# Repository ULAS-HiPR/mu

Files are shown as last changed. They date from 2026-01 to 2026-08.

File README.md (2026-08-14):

# Mu

Mu is a standalone SiPM/scintillator cosmic-ray detector and flight logger developed alongside the [Ogma avionics stack](https://sean-osullivan.com/projects/ogma/). It is designed to fly as its own black box: battery power in, particle and pressure data logged to onboard flash, then post-flight readout.

> [!CAUTION]
> **Rev 1 assembly corrections:** The `MICROFC-60035-SMT-TR1` SiPM footprint nets are reversed. On an existing Rev 1 PCB, mount U3 180 degrees from the orientation indicated by the footprint's pin-1 marker. This puts SiPM pin 3 (cathode) on PCB pad 1, the filtered HV-bias node, and SiPM pin 1 (anode) on PCB pad 3, the U5 inverting-input node. Pins 2 (fast output) and 4 (no connect) then exchange two unused PCB pads.
>
> The Rev 1 footprint also connects centre pad 5 to AGND. [Onsemi specifies pin 5 as no connect and recommends leaving the paddle unsoldered and floating](https://www.onsemi.com/download/data-sheet/pdf/microc-series-d.pdf). On the working board, a tiny piece of Blu Tack on the PCB beneath pad 5 kept the centre paddle off the board, and the sensor was attached to four small solder balls around the outer pads. A new PCB revision should correct the pin 1/pin 3 net mapping and leave pad 5 floating instead of relying on either assembly workaround.

## Hardware

- 50 x 50 x 20 mm BC-408 plastic scintillator.
- Onsemi MicroFC-60035 6 x 6 mm SiPM biased at about 30 V.
- OPA656/OPA814-class transimpedance readout around a 2.5 V reference.
- STM32F042 controller, W25Q128 external flash, and MS5607 barometer.
- Optional CAN interface; standalone logging does not depend on the Ogma stack.

## Repository

- `mu.kicad_sch`, `power.kicad_sch`, and `mu.kicad_pcb` - KiCad hardware design.
- `fabrication/` - Rev 1 manufacturing outputs.
- `Lib/` - project symbols, footprints, and 3D models.
- `SiPM Test Samples/` - raw oscilloscope samples.

Firmware, the field dashboard, and current flight preparation are on [`mu/f042-bringup`](https://github.com/ULAS-HiPR/mu/tree/mu/f042-bringup).

## Status

Mu has detected and logged real particle pulses on the bench and flew at Mach26, but it did not record a clean in-flight particle run. The reproduced fault is mechanical over-compression of the scintillator/SiPM stack. Packaging and flight validation remain in progress; Mu is not yet flight-proven.

## Manufacturing support

Rev 1 PCB fabrication was sponsored through [EasyEDA Education](https://easyeda.com/education) and manufactured by [JLCPCB](https://jlcpcb.com/). The board was designed in KiCad and imported into EasyEDA Pro for the sponsorship and manufacturing workflow.

## More information

See the [Mu project write-up](https://sean-osullivan.com/projects/mu/) for the detector, bring-up failures, pulse captures, and flight diagnosis.

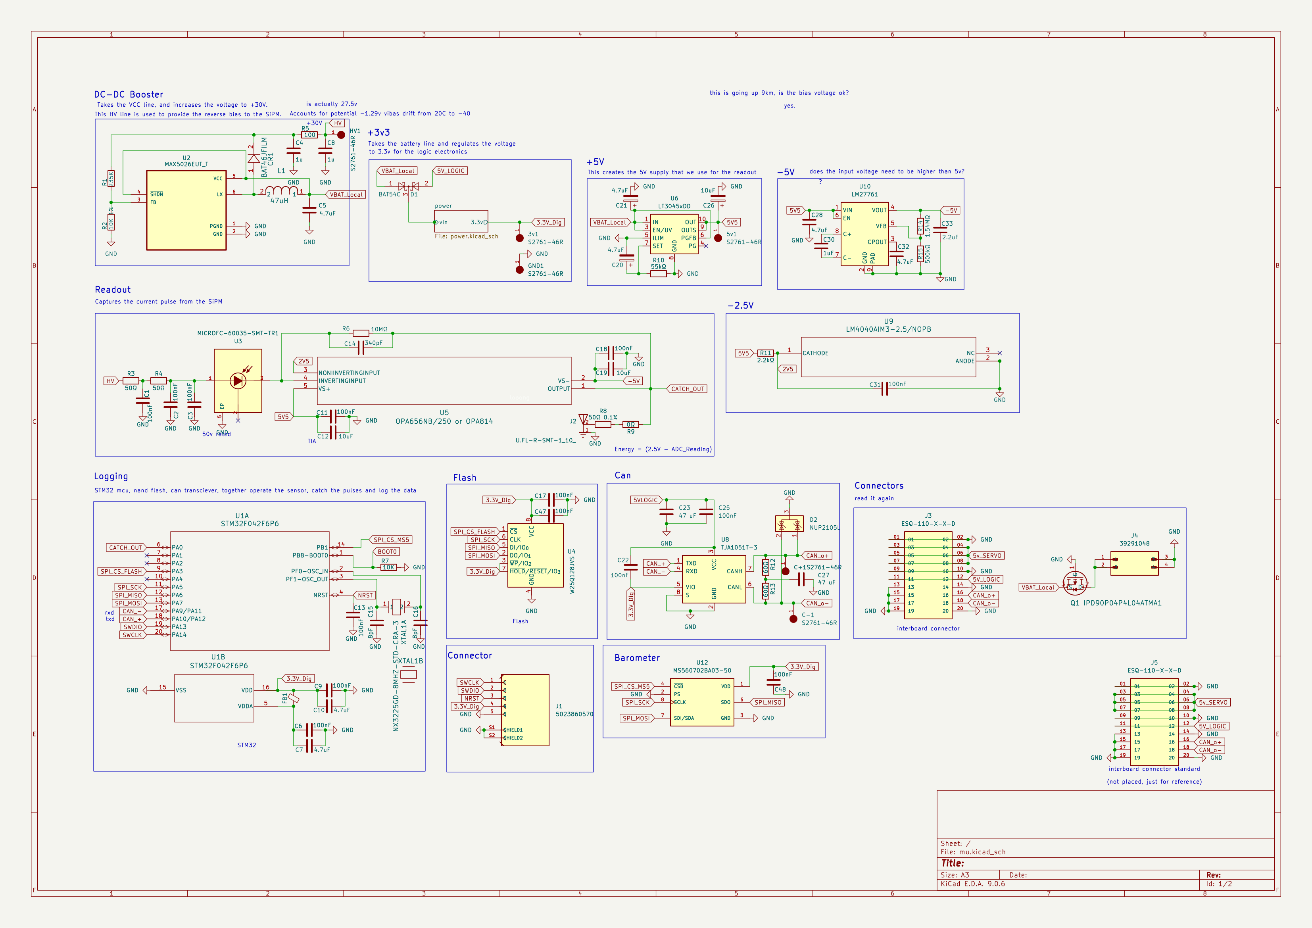
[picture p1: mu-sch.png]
Mu schematic


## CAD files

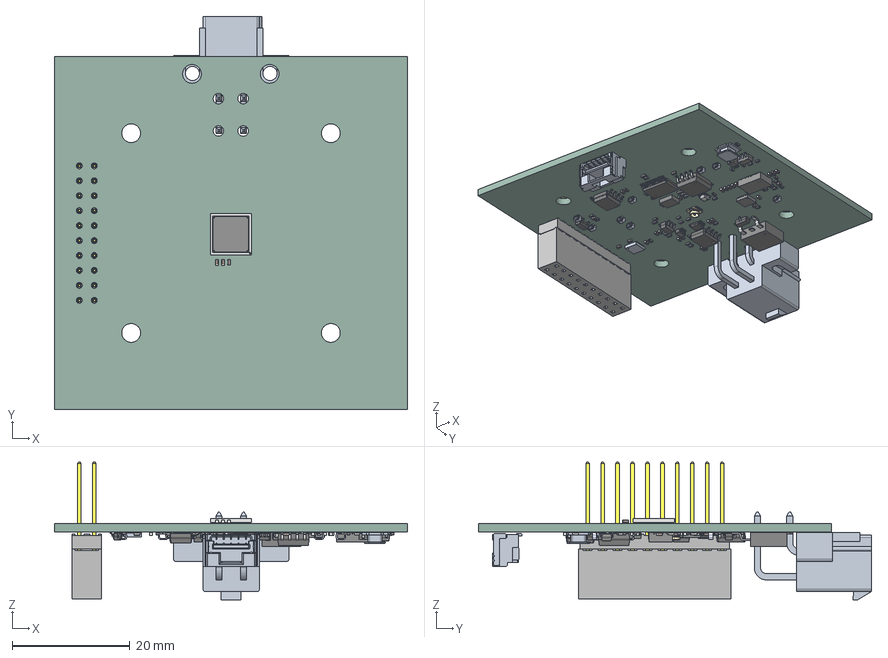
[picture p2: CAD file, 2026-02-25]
mu.step
60.0 x 66.8 x 23.4 mm
C_0402_1005Metric x 35
512AG_512AG
R_0402_1005Metric x 33
PG-TO252-3-313_INF
MAX5026EUT_T
SOIC-8-1EP_3.9x4.9mm_P1.27mm_EP2.29x3mm
L_0402_1005Metric
MPM3650CGQW
S2761-46R x 8
U.FL-R-SMT-1_10_
SOT-23 x 2
BMP390L--3DModel-STEP-510211
TSSOP-20_4.4x6.5mm_P0.65mm
LT3045EDD PBF Model
BODY-SOT
LEAD-SOT x 6
PIN1-ID
XTAL_NX3225GD-8MHZ-STD-CRA-3_NDK
SOT-23-5
ESQ-110-14-G-D-LL_socket
ESQ-110-14-G-D-LL_pins
ESQ-110-14-G-D-LL2_pins
ESQ-110-14-G-D-LL_bpins
SOIC-8_3.9x4.9mm_P1.27mm
SOIC-8_5.3x5.3mm_P1.27mm
mu 1.72.1
srn4018-3r3m
VSSOP-8_2.3x2mm_P0.5mm
SOD-323_STM
mu_PCB

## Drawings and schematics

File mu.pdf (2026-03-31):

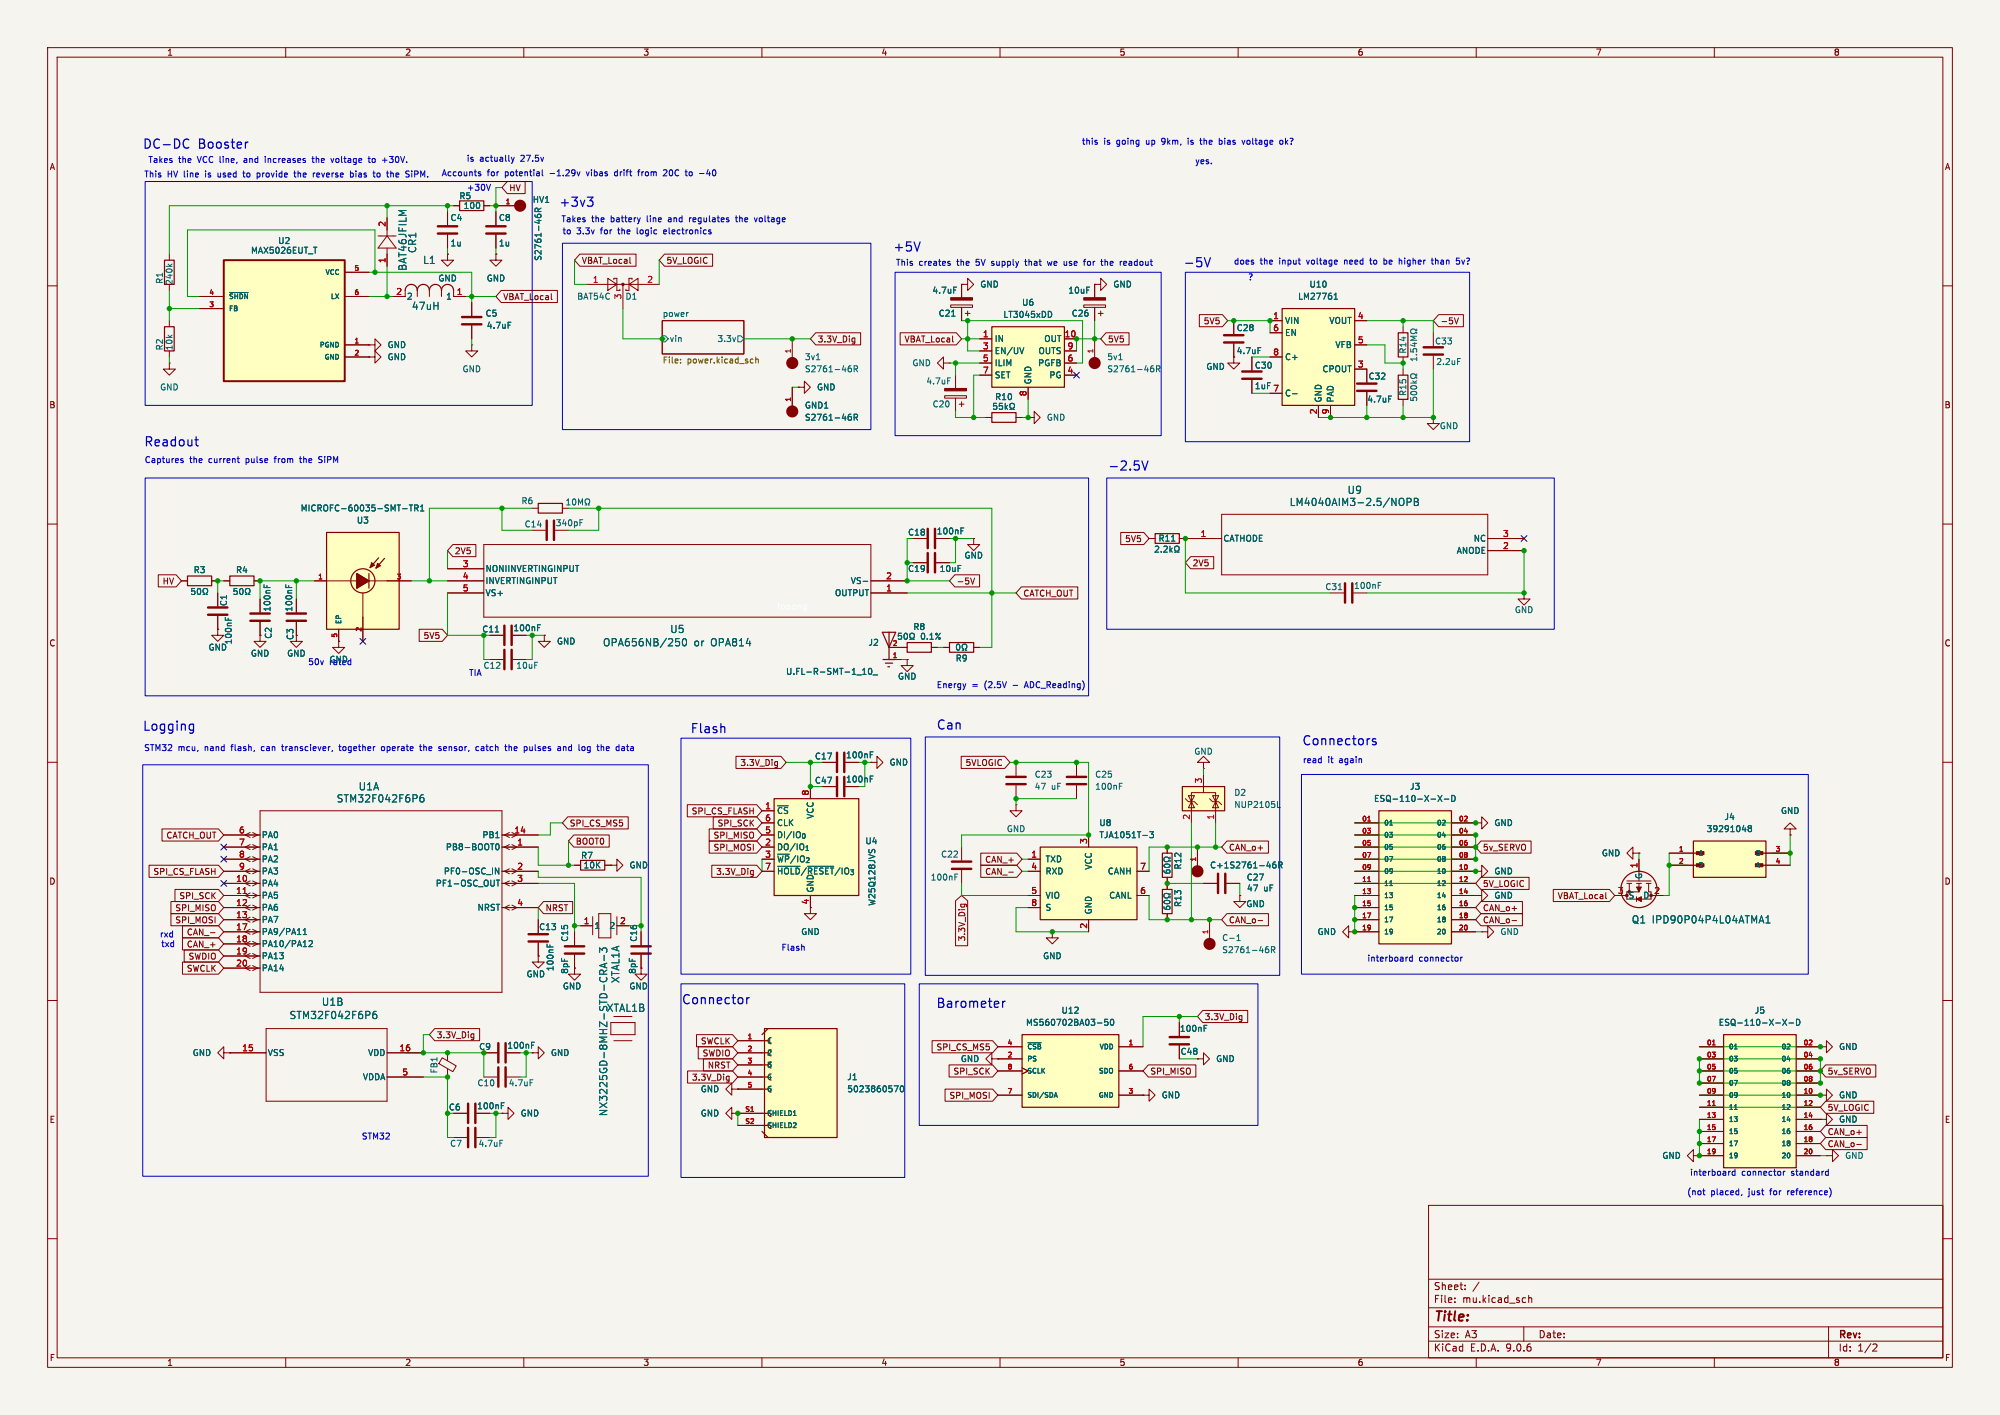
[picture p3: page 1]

this is going up 9km, is the bias voltage ok?

This creates the 5V supply that we use for the readout

does the input voltage need to be higher than 5v? Barometer

8 OUT 10 OUTS 9 PGFB 6 PG 4 U6
LT3045xDD

8 OUT 10 OUTS 9 PGFB 6 PG 4 R10

-2.5V Captures the current pulse from the SiPM Readout

3 GND GND GND GND

(not placed, just for reference) STM32

Id: 1/2 Title: File: mu.kicad_sch Sheet: /

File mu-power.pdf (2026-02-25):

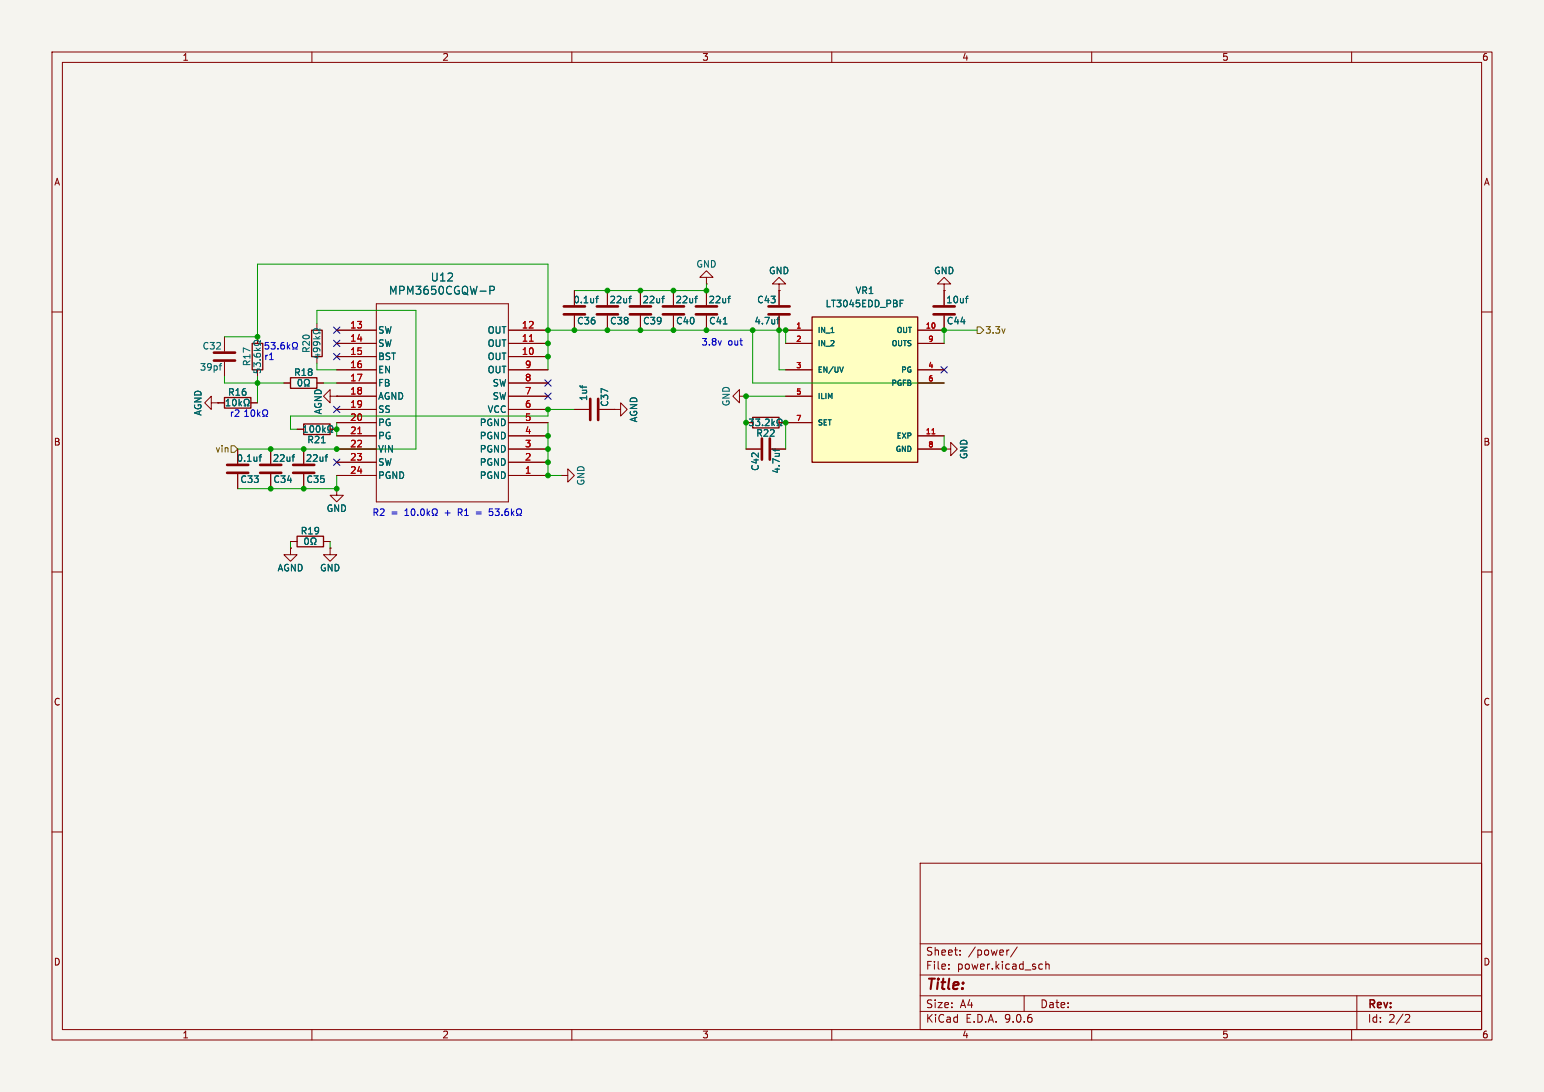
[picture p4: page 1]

Id: 2/2 Title: File: power.kicad_sch Sheet: /power/ GND

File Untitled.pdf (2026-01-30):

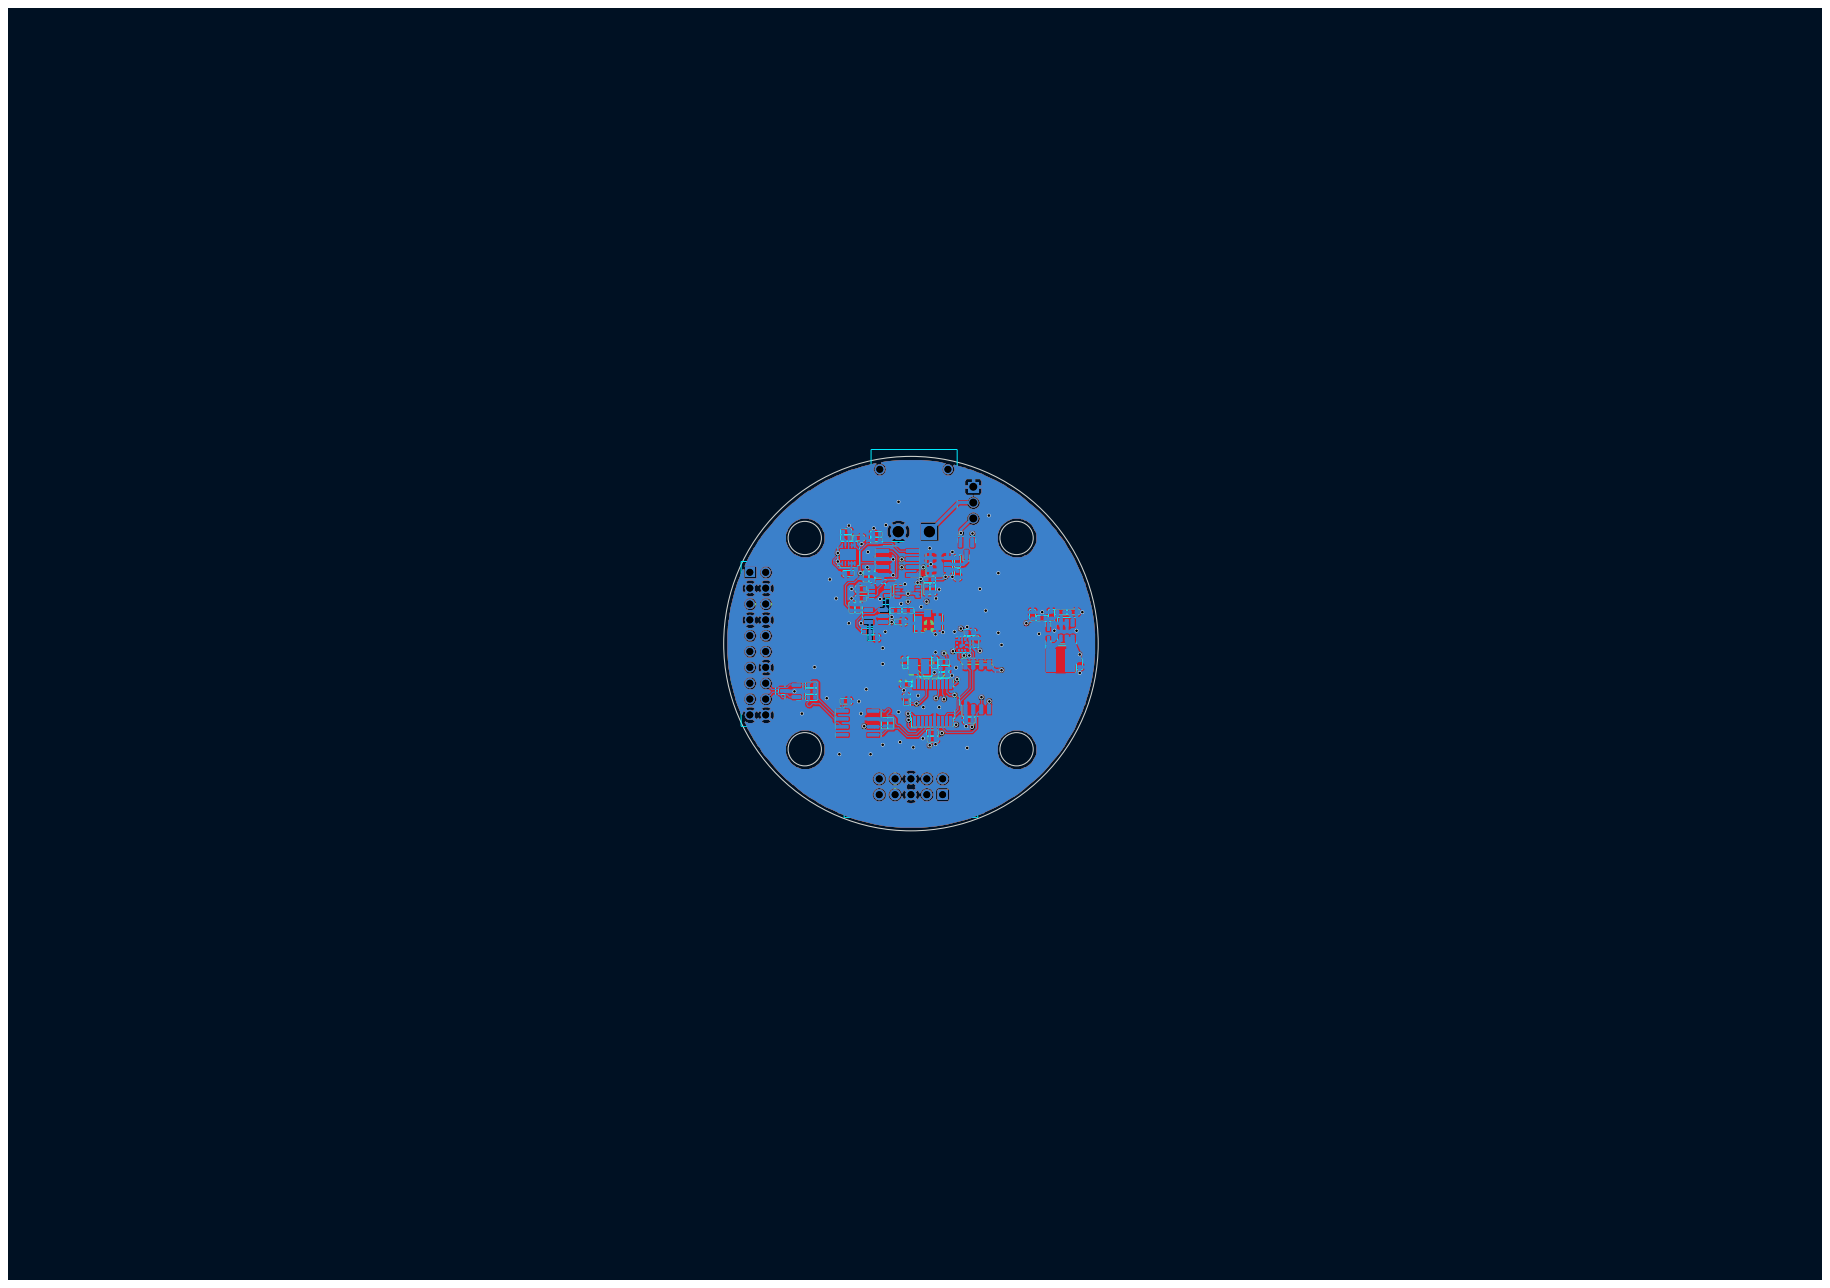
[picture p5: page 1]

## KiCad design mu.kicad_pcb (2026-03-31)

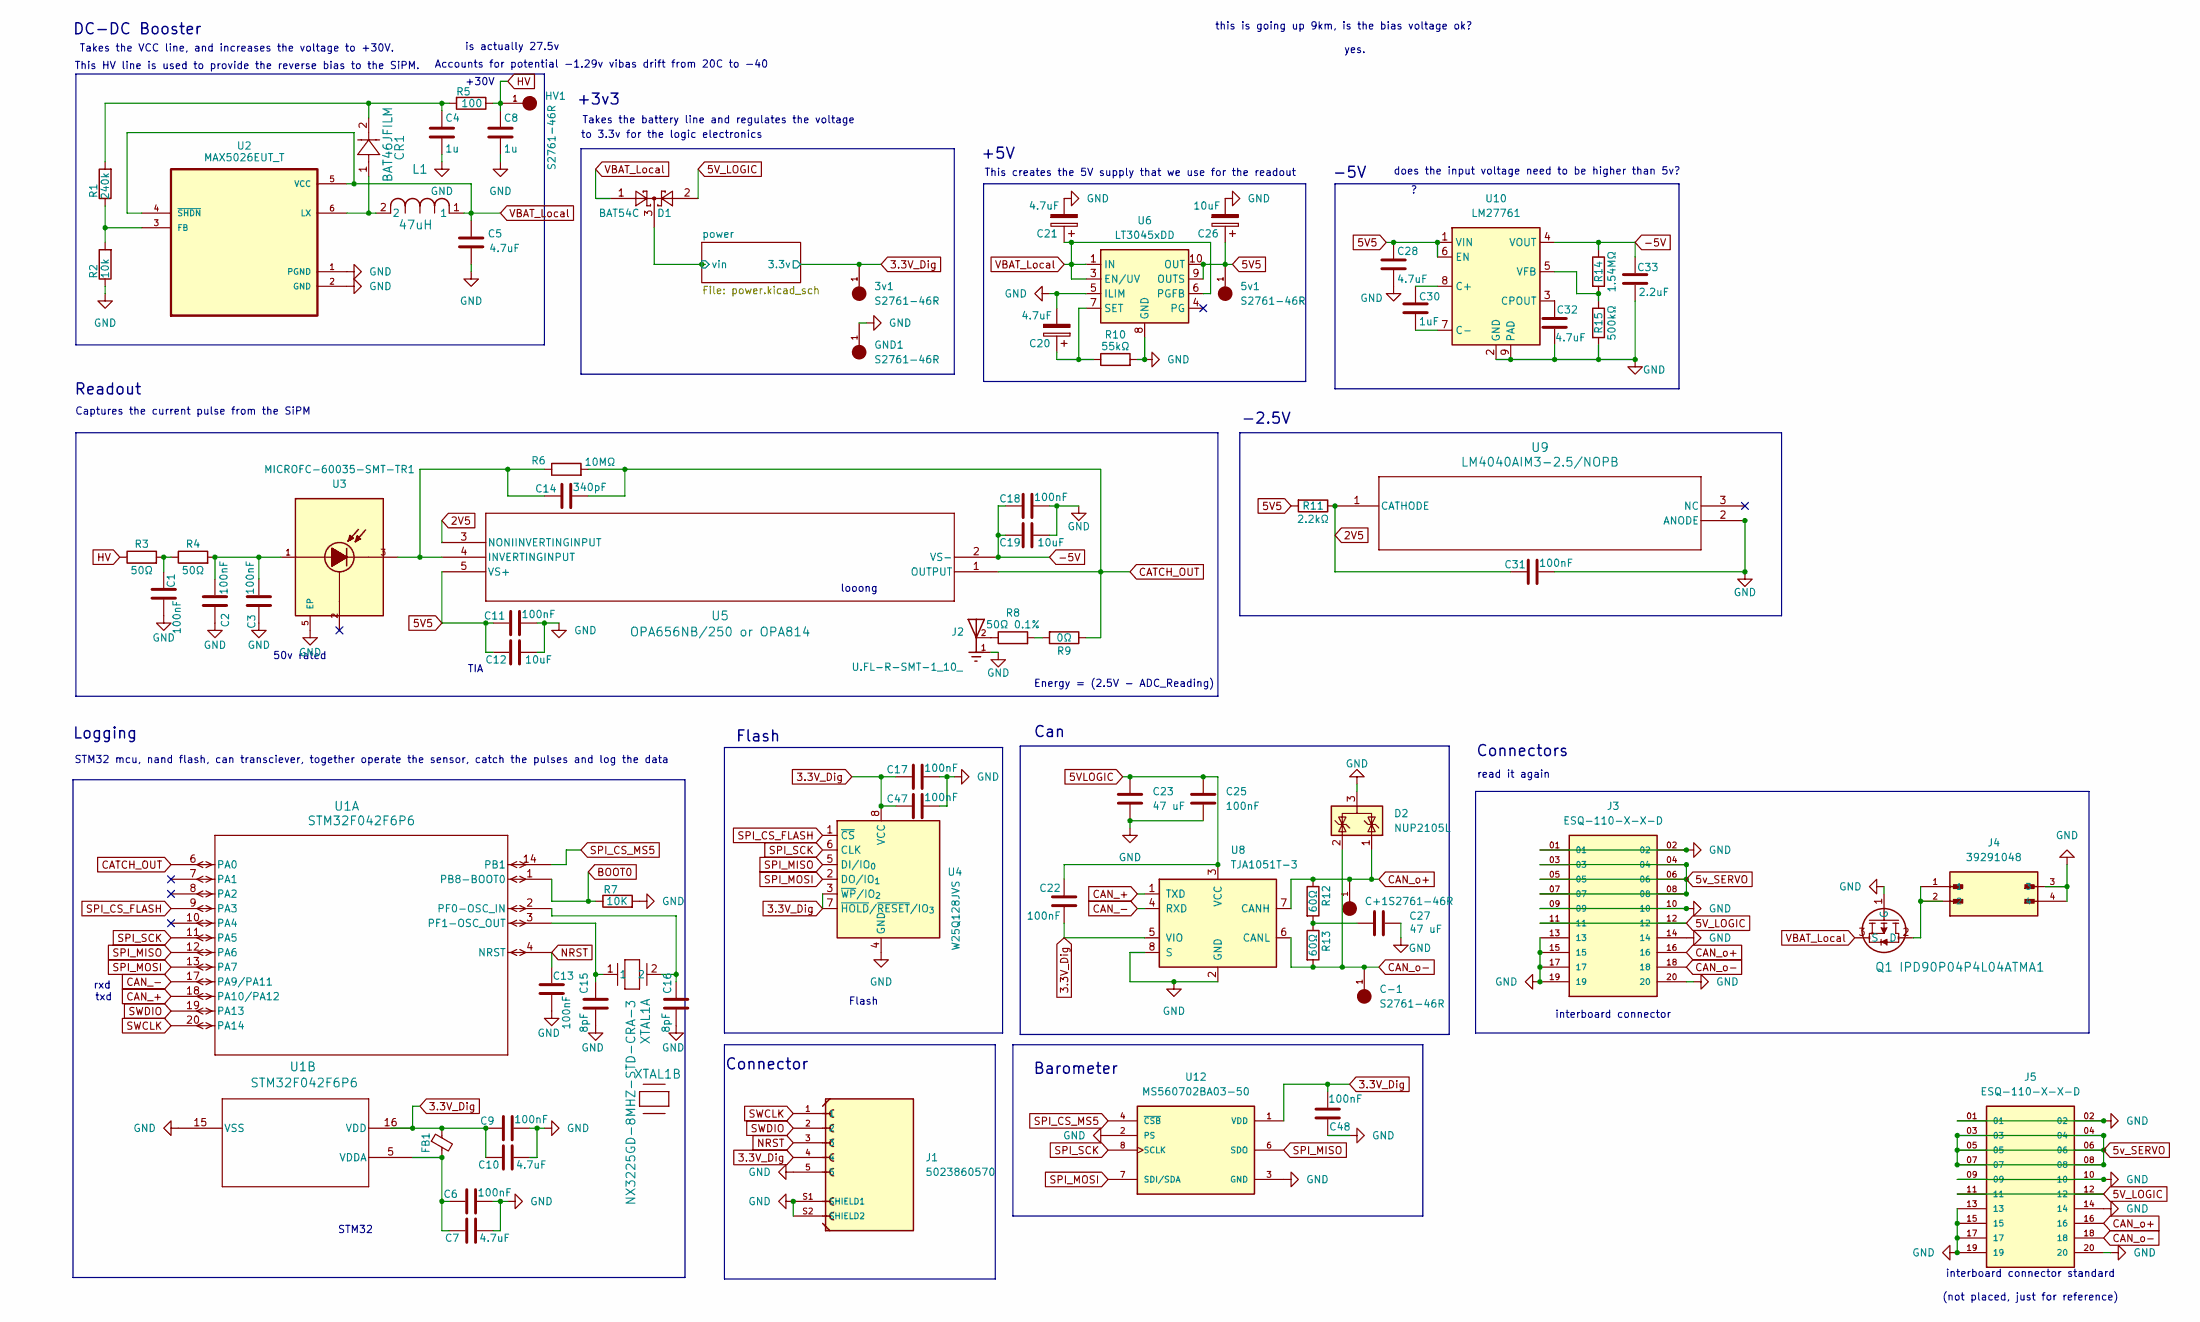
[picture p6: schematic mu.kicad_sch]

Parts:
3v1, 5v1: S2761-46R; HARWIN_S2761-46R; PARTREV 1
C1, C2, C3, C6, C9, C11, C13, C17, C18, C22, C25, C31, C47: 100nF; C_0402_1005Metric
C4, C8: 1u; R_0402_1005Metric
C5, C28, C32: 4.7uF; R_0402_1005Metric
C7, C10, C20, C21: 4.7uF; C_0402_1005Metric
C12: 10uF; C_0402_1005Metric
C14: 340pF; C_0402_1005Metric
C15, C16: 8pF; C_0402_1005Metric
C19, C26: 10uF; C_0603_1608Metric
C23, C27: 47 uF; C_0603_1608Metric
C30: 1uF; R_0402_1005Metric
C33: 2.2uF; C_0603_1608Metric
C48: 100nF; R_0402_1005Metric
C+1: S2761-46R; HARWIN_S2761-46R; PARTREV 1
C-1: S2761-46R; HARWIN_S2761-46R; PARTREV 1
CR1: BAT46JFILM; SOD-323_STM
D1: BAT54C; SOT-23
D2: NUP2105L; SOT-23
FB1: ferrite; L_0402_1005Metric
GND1: S2761-46R; HARWIN_S2761-46R; PARTREV 1
HV1: S2761-46R; HARWIN_S2761-46R; PARTREV 1
J1: 5023860570; MOLEX_5023860570; PARTREV F
J2: U.FL-R-SMT-1_10_; HRS_U.FL-R-SMT-1_10_
J3, J5: ESQ-110-X-X-D; SAMTEC_ESQ-110-14-G-D; PARTREV NA
J4: 39291048; MOLEX_39291048; PARTREV N1
L1: 47uH; IND_BOURNS_SRN4018
Q1: IPD90P04P4L04ATMA1; PG-TO252-3-313_INF-L
R1: 240k; R_0402_1005Metric
R2: 10k; R_0402_1005Metric
R3, R4: 50Ω; R_0402_1005Metric
R5: 100; R_0402_1005Metric
R6: 10MΩ; R_0402_1005Metric
R7: 10K; R_0402_1005Metric
R8: 50Ω 0.1%; R_0402_1005Metric
R9: 0Ω; R_0402_1005Metric
R10: 55kΩ; R_0402_1005Metric
R11: 2.2kΩ; R_0402_1005Metric
R12, R13: 60Ω; R_0402_1005Metric
R14: 1.54MΩ; R_0402_1005Metric
R15: 500kΩ; R_0402_1005Metric
U1: STM32F042F6P6; TSSOP20
U2: MAX5026EUT_T; SOT95P280X145-6N
U3: MICROFC-60035-SMT-TR1; XDCR_MICROFC-60035-SMT-TR1; PARTREV 31 JUL 2018
U4: W25Q128JVS; SOIC-8_5.3x5.3mm_P1.27mm
U5: OPA656NB/250 or OPA814; DBV5
U6: LT3045xDD; DFN-10-1EP_3x3mm_P0.5mm_EP1.65x2.38mm
U8: TJA1051T-3; SOIC-8_3.9x4.9mm_P1.27mm
U9: LM4040AIM3-2.5/NOPB; DBZ3
U10: LM27761; WSON-8-1EP_2x2mm_P0.5mm_EP0.9x1.6mm
U12: MS560702BA03-50; SON125P300X500X100-8N
XTAL1: NX3225GD-8MHZ-STD-CRA-3; XTAL_NX3225GD-8MHZ-STD-CRA-3_NDK

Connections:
2V5: C31.1, R11.1, U5.3 (NONIINVERTINGINPUT), U9.1 (CATHODE)
3.3V_Dig: 3v1.1, C9.1, C10.1, C17.1, C22.1, C47.1, C48.2, FB1.1, J1.4, U1.16 (VDD), U4.3 (~WP/IO_{2}), U4.7 (~HOLD/~RESET/IO_{3}), U4.8 (VCC), U8.5 (VIO), U12.1 (VDD); also elsewhere on the board
5V5: 5v1.1, C11.1, C12.1, C26.1, C28.1, R11.2, U5.5 (VS+), U6.9 (OUTS), U6.10 (OUT), U10.1 (VIN), U10.6 (EN); also elsewhere on the board
5VLOGIC: C22.2, C23.1, C25.1, U8.3 (VCC)
5V_LOGIC: D1.2, J3.11, J3.12, J5.11, J5.12
5v_SERVO: J3.03, J3.04, J3.05, J3.06, J3.07, J3.08, J5.03, J5.04, J5.05, J5.06, J5.07, J5.08
-5V: C18.1, C19.1, C33.1, R14.1, U5.2 (VS-), U10.4 (VOUT)
/power/vin: D1.3; also elsewhere on the board
AGND: C1.2, C2.2, C3.1, C4.2, C5.2, C6.2, C7.2, C8.2, C9.2, C10.2, C11.2, C12.2, C13.2, C15.1, C16.2, C17.2, C18.2, C19.2, C20.2, C21.2, C23.2, C25.2, C26.2, C27.2, C28.2, C31.2, C32.2, C33.2, C47.2, C48.1, D2.3 (A), GND1.1, J1.5, J1.S1 (SHIELD1), J1.S2 (SHIELD2), J2.1, J2.3, J3.01, J3.02, J3.09, J3.10, J3.13, J3.14, J3.15, J3.17, J3.19, J3.20, J4.3, J4.4, J5.01, J5.02, J5.09, J5.10, J5.13, J5.14, J5.15, J5.17, J5.19, J5.20, Q1.1 (G), R2.1, R7.2, R10.2, R15.2, U1.15 (VSS), U2.1 (PGND), U2.2 (GND), U3.5 (EP), U4.4 (GND), U6.5 (ILIM), U6.8 (GND), U6.11 (GND), U8.2 (GND), U8.8 (S), U9.2 (ANODE), U10.2 (GND), U10.9 (PAD), U12.2 (PS), U12.3 (GND); also elsewhere on the board
BOOT0: R7.1, U1.1 (PB8-BOOT0)
CAN_+: U1.18 (PA10/PA12), U8.1 (TXD)
CAN_-: U1.17 (PA9/PA11), U8.4 (RXD)
CAN_o+: C+1.1, D2.1 (K), J3.16, J5.16, R12.1, U8.7 (CANH); also elsewhere on the board
CAN_o-: C-1.1, D2.2 (K), J3.18, J5.18, R13.2, U8.6 (CANL); also elsewhere on the board
CATCH_OUT: C14.2, R6.2, R9.1, U1.6 (PA0), U5.1 (OUTPUT)
HV: C8.1, HV1.1, R3.1, R5.1; also elsewhere on the board
NRST: C13.1, J1.3, U1.4 (NRST)
unnamed: C1.1, R3.2, R4.1
unnamed: C2.1, C3.2, R4.2, U3.1
unnamed: C4.1, CR1.2, R1.2, R5.2
unnamed: C27.1, R12.2, R13.1
unnamed: J2.2, R8.1
unnamed: J4.1, J4.2, Q1.2 (D)
unnamed: R8.2, R9.2
unnamed: C16.1, U1.2 (PF0-OSC_IN), XTAL1.2
unnamed: C15.2, U1.3 (PF1-OSC_OUT), XTAL1.1
unnamed: C6.1, C7.1, FB1.2, U1.5 (VDDA)
unnamed: R1.1, R2.2, U2.3 (FB)
unnamed: CR1.1, L1.2, U2.6 (LX)
unnamed: C14.1, R6.1, U3.3, U5.4 (INVERTINGINPUT)
unnamed: C20.1, R10.1, U6.7 (SET)
unnamed: C30.1, U10.8 (C+)
unnamed: C30.2, U10.7 (C-)
unnamed: C32.1, U10.3 (CPOUT)
unnamed: R14.2, R15.1, U10.5 (VFB)
SPI_CS_FLASH: U1.9 (PA3), U4.1 (~CS)
SPI_CS_MS5: U1.14 (PB1), U12.4 (~CSB), U12.5 (~CSB)
SPI_MISO: U1.12 (PA6), U4.5 (DI/IO_{0}), U12.6 (SDO)
SPI_MOSI: U1.13 (PA7), U4.2 (DO/IO_{1}), U12.7 (SDI/SDA)
SPI_SCK: U1.11 (PA5), U4.6 (CLK), U12.8 (SCLK)
SWCLK: J1.1, U1.20 (PA14)
SWDIO: J1.2, U1.19 (PA13)
VBAT_Local: C5.1, C21.1, D1.1, L1.1, Q1.3 (S), U2.4 (~SHDN), U2.5 (VCC), U6.1 (IN), U6.2 (IN), U6.3 (EN/UV), U6.6 (PGFB)

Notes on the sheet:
Takes the battery line and regulates the voltage
looong
rxd
read it again
txd
TIA
Barometer
-5V
interboard connector
DC-DC Booster
-2.5V
Flash
does the input voltage need to be higher than 5v?
interboard connector standard (not placed, just for reference)
STM32 mcu, nand flash, can transciever, together operate the sensor, catch the pulses and log the data
Logging
50v rated
Flash
+3v3
this is going up 9km, is the bias voltage ok? yes.
Readout
This HV line is used to provide the reverse bias to the SiPM.
Takes the VCC line, and increases the voltage to +30V.
This creates the 5V supply that we use for the readout
Connector
is actually 27.5v
Can
+5V
to 3.3v for the logic electronics
Captures the current pulse from the SiPM
Accounts for potential -1.29v vibas drift from 20C to -40
+30V
Connectors
Energy = (2.5V - ADC_Reading)
STM32

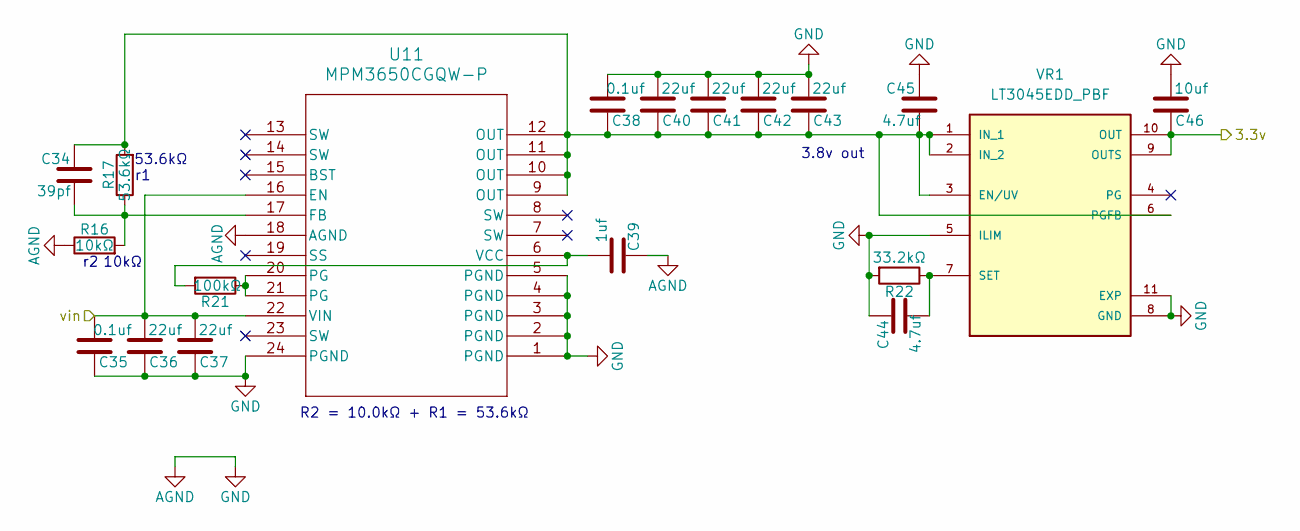
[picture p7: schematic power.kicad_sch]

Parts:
C34: 39pf; C_0402_1005Metric
C35, C38: 0.1uf; C_0402_1005Metric
C36, C37, C40, C41, C42, C43: 22uf; C_0603_1608Metric
C39: 1uf; C_0402_1005Metric
C44, C45: 4.7uf; C_0402_1005Metric
C46: 10uf; C_0603_1608Metric
R16: 10kΩ; R_0402_1005Metric
R17: 53.6kΩ; R_0402_1005Metric
R21: 100kΩ; R_0402_1005Metric
R22: 33.2kΩ; R_0402_1005Metric
U11: MPM3650CGQW-P; QFN-24_MPM3650_MNP
VR1: LT3045EDD_PBF; SON50P300X300X80-11N; PARTREV C

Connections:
3.3V_Dig: C46.1, VR1.9 (OUTS), VR1.10 (OUT); also elsewhere on the board
/power/vin: C35.2, C36.2, C37.2, U11.16 (EN), U11.22 (VIN); also elsewhere on the board
AGND: C35.1, C36.1, C37.1, C38.2, C39.1, C40.2, C41.2, C42.2, C43.2, C44.1, C45.1, C46.2, R16.1, R22.2, U11.1 (PGND), U11.2 (PGND), U11.3 (PGND), U11.4 (PGND), U11.5 (PGND), U11.18 (AGND), U11.24 (PGND), VR1.5 (ILIM), VR1.8 (GND), VR1.11 (EXP); also elsewhere on the board
unnamed: R21.1, U11.20 (PG), U11.21 (PG)
unnamed: C34.2, R16.2, R17.1, U11.17 (FB)
unnamed: C39.2, R21.2, U11.6 (VCC)
unnamed: C34.1, C38.1, C40.1, C41.1, C42.1, C43.1, C45.2, R17.2, U11.9 (OUT), U11.10 (OUT), U11.11 (OUT), U11.12 (OUT), VR1.1 (IN_1), VR1.2 (IN_2), VR1.3 (EN/UV), VR1.6 (PGFB)
unnamed: C44.2, R22.1, VR1.7 (SET)

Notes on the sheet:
10kΩ
53.6kΩ
R2 = 10.0kΩ + R1 = 53.6kΩ
3.8v out

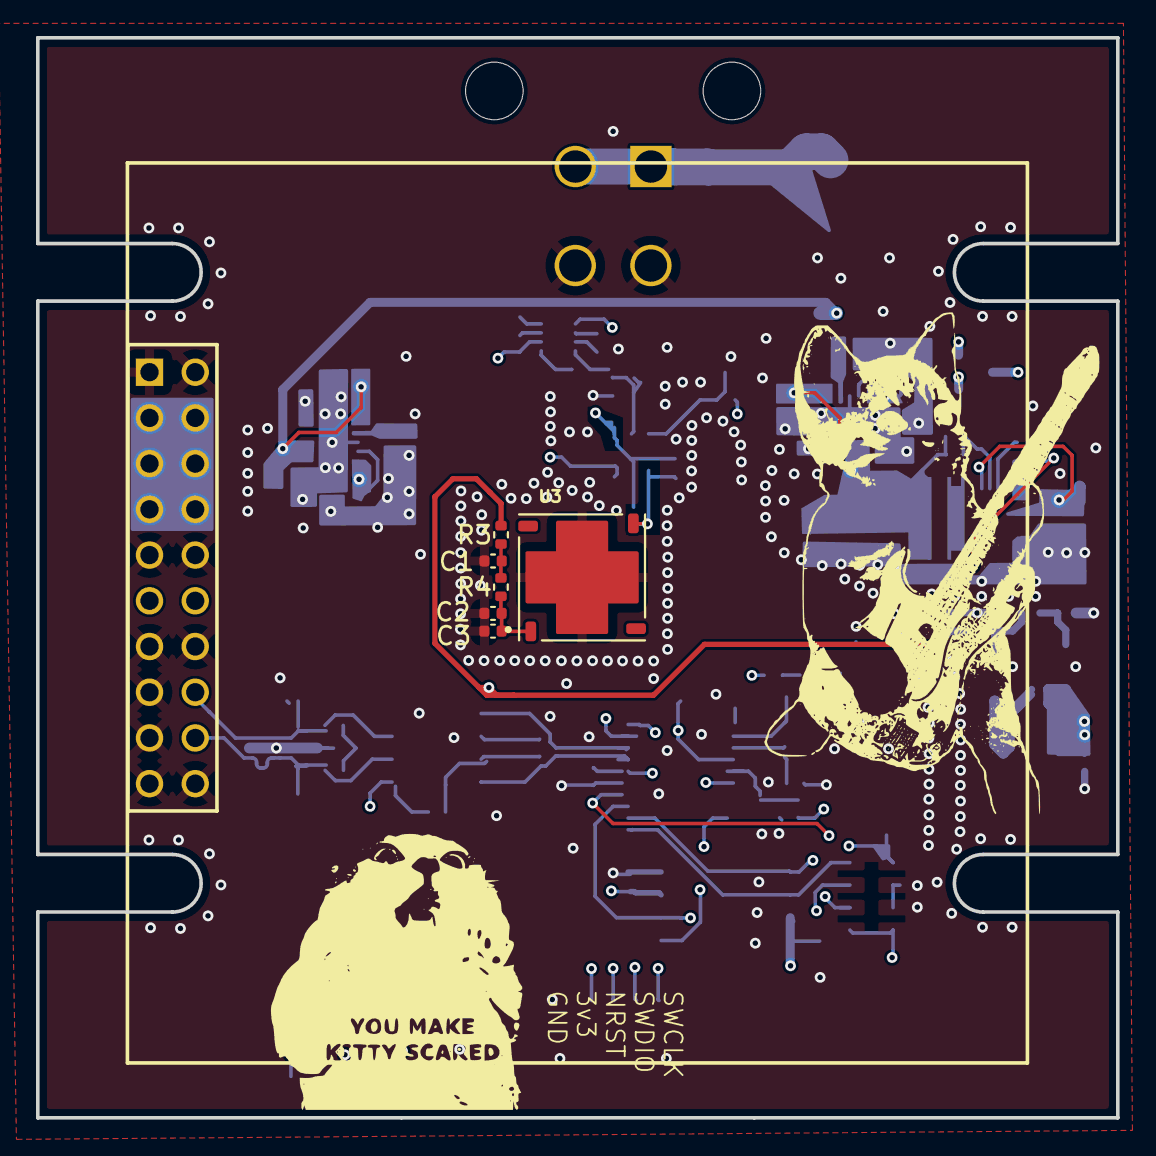
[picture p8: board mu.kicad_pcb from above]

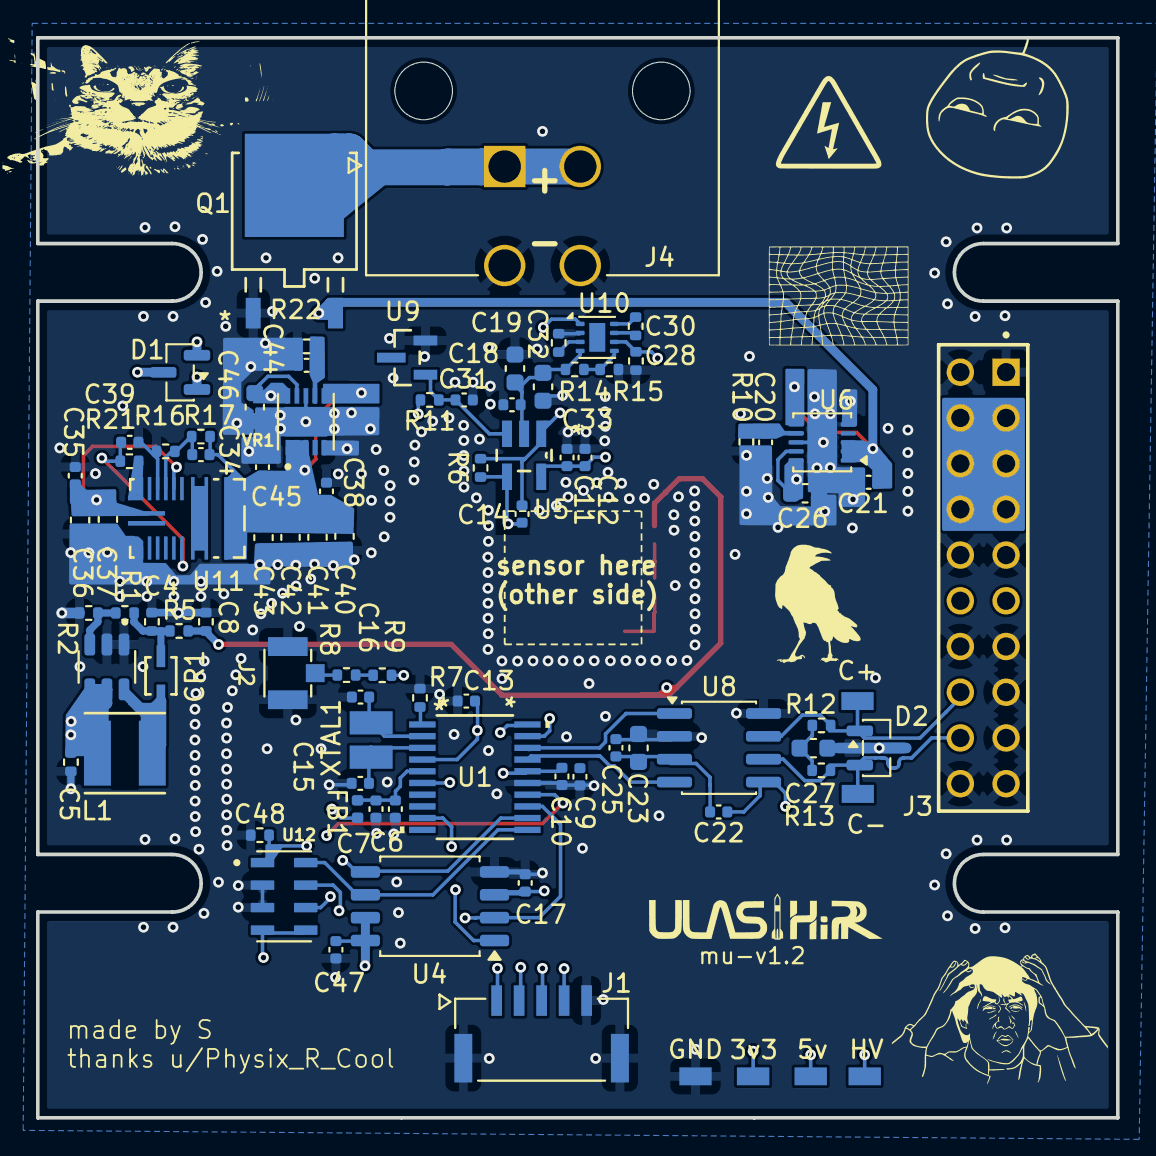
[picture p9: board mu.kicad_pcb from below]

Board: 6 copper layers, 60.0 x 60.0 mm, 94 parts (88 on the bottom side), 48 nets.

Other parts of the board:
3v3, 5v: S2761-46R; HARWIN_S2761-46R
C+: S2761-46R; HARWIN_S2761-46R
C-: S2761-46R; HARWIN_S2761-46R
GND: S2761-46R; HARWIN_S2761-46R
HV: S2761-46R; HARWIN_S2761-46R

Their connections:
3.3V_Dig: 3v3.1; also elsewhere on the board
5V5: 5v.1; also elsewhere on the board
AGND: GND.1; also elsewhere on the board
CAN_o+: C+.1; also elsewhere on the board
CAN_o-: C-.1; also elsewhere on the board
HV: HV.1; also elsewhere on the board

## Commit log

2025-12-14 imported first component
    [mu.kicad_pcb, mu.kicad_sch]
2025-12-17 big progress, superfluous caps added
    [mu.kicad_sch]
2025-12-17 sent v1 to stephen
    [mu.kicad_sch]
2025-12-17 push before fabien
    [mu.kicad_pcb, mu.kicad_sch, mu.step]
2025-12-24 huge progress, caught issue
    [mu.kicad_pcb, mu.kicad_sch]
2025-12-25 nearly ready for layout
    [mu.kicad_sch]
2025-12-26 svgs for readmes
    [mu.kicad_sch]
2025-12-28 added usb c and fixed many silly issues
    [mu.kicad_sch]
2025-12-28 flipflop is 3v3
    [mu.kicad_sch]
2025-12-28 esd protection
    [mu.kicad_pcb, mu.kicad_sch]
2025-12-28 schematic locked in, connenctors added
    [mu.kicad_sch]
2025-12-29 ready to place
    [mu.kicad_pcb, mu.kicad_sch]
2026-01-06 layout rocking
    [mu.kicad_pcb]
2026-01-14 nearly done now
    [mu.kicad_pcb, mu.kicad_sch]
2026-01-15 restructuring now that we've got the standard connector
    [mu.kicad_pcb, mu.kicad_sch]
2026-01-15 restructuring now that we've got the standard connector part 2
    [mu.kicad_pcb]
2026-01-15 routed fully, pending final checks
    [mu.kicad_pcb]
2026-01-15 ready for review
    [mu.kicad_pcb]
2026-01-15 programming stuff
    [mu.kicad_pcb, mu.kicad_sch]
2026-01-16 ready to send off to stephen
    [mu-B_Cu.gbr, mu-B_Mask.gbr, mu-B_Paste.gbr, mu-B_Silkscreen.gbr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]
2026-01-16 higher voltage diode
    [mu-B_Cu.gbr, mu-B_Mask.gbr, mu-B_Paste.gbr, mu-B_Silkscreen.gbr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]
2026-01-19 ready to rock and roll
    [mu.kicad_pcb, mu.kicad_sch]
2026-01-21 refactored following thoughts
    [mu.kicad_pcb, mu.kicad_sch]
2026-01-22 xt30 added
    [mu.kicad_pcb, mu.kicad_sch]
2026-01-22 spacer prints
    [mu.kicad_pcb]
2026-01-22 fixed the connector
    [mu.kicad_pcb, mu.kicad_sch]
2026-01-27 major revisions
    [mu.kicad_pcb, mu.kicad_sch]
2026-01-27 added the label
    [mu.kicad_pcb]
2026-01-30 drc pass
    [mu-B_Cu.gbr, mu-B_Mask.gbr, mu-B_Paste.gbr, mu-Edge_Cuts.gbr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]
2026-01-30 thermal expansion vias
    [mu.kicad_pcb]
2026-02-03 3d model made
    [mu.kicad_sch, mu.step]
2026-02-05 refdes, test points, better connector
    [mu.kicad_pcb, mu.kicad_sch]
2026-02-05 power subschematic done
    [mu.kicad_pcb, mu.kicad_sch, power.kicad_sch]
2026-02-06 cleaned some more
    [mu.kicad_pcb]
2026-02-09 lots done
    [mu.kicad_pcb, mu.kicad_sch]
2026-02-10 ready for upload
    [mu.kicad_pcb, mu.kicad_sch, power.kicad_sch]
2026-02-25 ready for review the twost, nearly
    [mu.kicad_pcb, mu.kicad_sch, mu.step, power.kicad_sch]
2026-02-26 ready for review the twost, nearly, readout locked
    [mu.kicad_sch, power.kicad_sch]
2026-02-26 ready for review the twost, nearly, readout locked :)
    [mu.kicad_pcb, mu.kicad_sch]
2026-02-26 ready for review the twost, nearly, readout locked :), for real
    [mu.kicad_pcb]
2026-02-27 ready to go, nearly
    [mu-B_Cu.gbr, mu-B_Mask.gbr, mu-B_Paste.gbr, mu-B_Silkscreen.gbr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]
2026-03-01 ready 2 order
    [mu-job.gbrjob, mu.kicad_pcb, mu.kicad_sch, power.kicad_sch]
2026-03-31 hardware done
    [mu-job.gbrjob, mu.kicad_pcb, mu.kicad_sch, power.kicad_sch]
